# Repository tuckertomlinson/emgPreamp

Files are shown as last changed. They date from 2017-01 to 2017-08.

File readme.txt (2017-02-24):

#Boilerplate:
The files in this repository are my attempt to produce a high-quailty,
buffering amplifier for EMG signals in the laboratory environment. I
am NOT a hardware designer by trade and have not necessarily tested
any of the supplied files for my own purposes, much less yours. I 
make no garauntees that these circuits will be useful or even 
functional.

It is important to also note: I have not designed these
to comply with any FDA standards. Any compliance with said standards
is purely coincidental. These designs are inteded for animal research
and are NOT fit for human recordings in the clinical environment. 

If you choose to use these designs, it is incumbent on you to evaluate
the schematics and test them to ensure they are adequate, in both 
performance and safety, for your task.

I make no promise of support, however, you are welcome to shoot me
an email if you want to use these designs. I might be able to answer
some simple questions.

#The project:
-I need to record 24 differential EMG signals from intramuscular wires
-My signals of interest are in the +/-10mV range
-My ADC system has a +/-5V range, and is remote from the signal source
-I need to buffer and amplify my signals at the source to avoid line
artifacts in my recordings
-The source of the signal is a 50pin samtec 0.05" connector, which I 
	want to convert to something sane like a DB style connector
	so I can use standard cables with my amplified signals

#the solution:
-Signal source connects to a backplane card
-backplane has 6x16pin header sockets 
-each header socket accepts a daughter card that contains 4 differential channels
-Connection to external systems is via DB37 connector
  -24 signal out lines
  -GND and external power in (optional)
  -reference rail out
-daughter cards take:
  - 8 lines of input signal (4 differential signals), 
  - a ground rail, 
  - a power rail
    -the power rail should be in the 5-18V range
  -and a reference rail.
    -the reference rail should be ~ halfway between the ground and power rails
-daughter cards output:
  -4 lines of amplified differential signal centered on the reference rail
-Backplane has a 5pin header socket that is the source of the ground, power and reference rails
  -power connection to external systems will depend on the DAC format you use
  -for a 0V centered ADC (e.g. +/-5V), isolate the ground and power rails from the world, and short the reference to the ADC ground
  -for a positive biased ADC (e.g. 0-10V), connect the ground rail to the DAC ground, and the reference rail to one of the ADC inputs
    -logging the voltage of VRef allows you to subtract in software, recovering the true differential signal
  -The easiest power solution is to simply use 2x 9V batteries in series
    -Power rail is 18V, reference rail is 9V
  -included in the project is a schematic for a power conditioning card
    -card takes in 12-15V power
    -Isolates to internal 12V rail via switchmode isolation supply
    -Uses filters and linear regulators to supply 10V power rail and 5v reference rail to backplane
    -power rail, backplane ground and reference rail are isolated from the supplied power.

The circuit schematics for this project are built in Eagle. 
I have tried to label the lines in each PCB in a sane way, so it should be possible to sort out what's going on. 

In some cases I have needed to create a custom part based on other 
existing libraries in order to get the correct footprint and pinout. 
I have not explicitly included those libraries in this project.

Currently the backplane and daughter cards are tested and functioning as designed. With implanted EMG wires it is common to see single motor unit acticity in the EMG signal. The power-conditioning board is not yet tested

Tucker Tomlinson
tuckertomlinson@gmail.com
Jan 25 2017

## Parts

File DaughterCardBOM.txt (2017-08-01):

item:				supplier:		part number:		notes:
1xPCB				OSH Park		-			OSH accepts eagle files directly, so you can simply upload the brd file to their website
1xsolder mask			OSH stencil		-			you can skip this and apply solder paste by hand, but will have much higher rate of solder-flow errors, particularly under the QVFN-16 amp chips
2x AD8224 instrumentation amp	digikey			AD8224ACPZ-R7CT-ND 	The AD8222 is a pin compatible part with slightly different characteristics (higher gain capability, better CMRR, higher bias current), that may be substituted if desired
1x 2x8pin M 90deg header	digikey			609-3337-ND
8x .01uF 0805 capacitor		digikey			1276-1007-1-ND 		decoupling cap for inputs to amps. no particularly high tolerances needed.
4x 100pF 0805 capacitor		digikey			478-10493-1-ND		RF suppression cap for input lines. Should be significantly lower impedance than caps on input lines.
8x 10k 0.1% 0805 resistor	digikey			P10KDACT-ND		.1% is probably not necessary, but for low volume production, its worth a few extra dollars to match everything
8x 4700pF 1% NP0 0805 capacitor	digikey			490-8288-1-ND		the 1% tolerance isn't necessary, but you need to match capacitor values as well as possible, and the minor increase in cost is offset by the labor savings matching caps
8x 1M 0.1% 0805 resistor	digikey			P1MDACT-ND 		the 0.1% tolerance isn't necessary, but you need to match resistor values as well as possible, and the minor increase in cost is offset by the labor savings matching resistors
4x 499ohm 0805 resistor		digikey			P499CCT-ND 		These set the gain at 100x. Check the AD8224 datasheet to select the correct resistor for alternate gain settings 
4x 49.9ohm 0805 resistor	digikey			P49.9CCT-ND 		inline with output to inhibit ringing

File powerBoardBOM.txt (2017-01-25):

item:				supplier:		part number:		notes:
1xPCB				OSH Park		-			OSH accepts eagle files directly, so you can simply upload the brd file to their website
2x ferrite bead			digikey			732-6713-1-ND 
2x 22uF 16V capacitor		digikey			1276-2909-1-ND 
2x 1uF capacitor		digikey			490-1691-1-ND 
2x 0.33ohm resistor		digikey			RL12S.33FCT-ND
1x 7805 regulator TO252		digikey			MC7805BDTRKGOSCT-ND
1x 7810 regulator TO252		digikey			296-19534-1-ND
1x 12V switchmode isolator	digikey			1470-2537-5-ND		this is a through hole component, but we solder it to the SMT pads, hanging off the board, for packaging
1x 5pin 90deg header		digikey			3M9307-ND

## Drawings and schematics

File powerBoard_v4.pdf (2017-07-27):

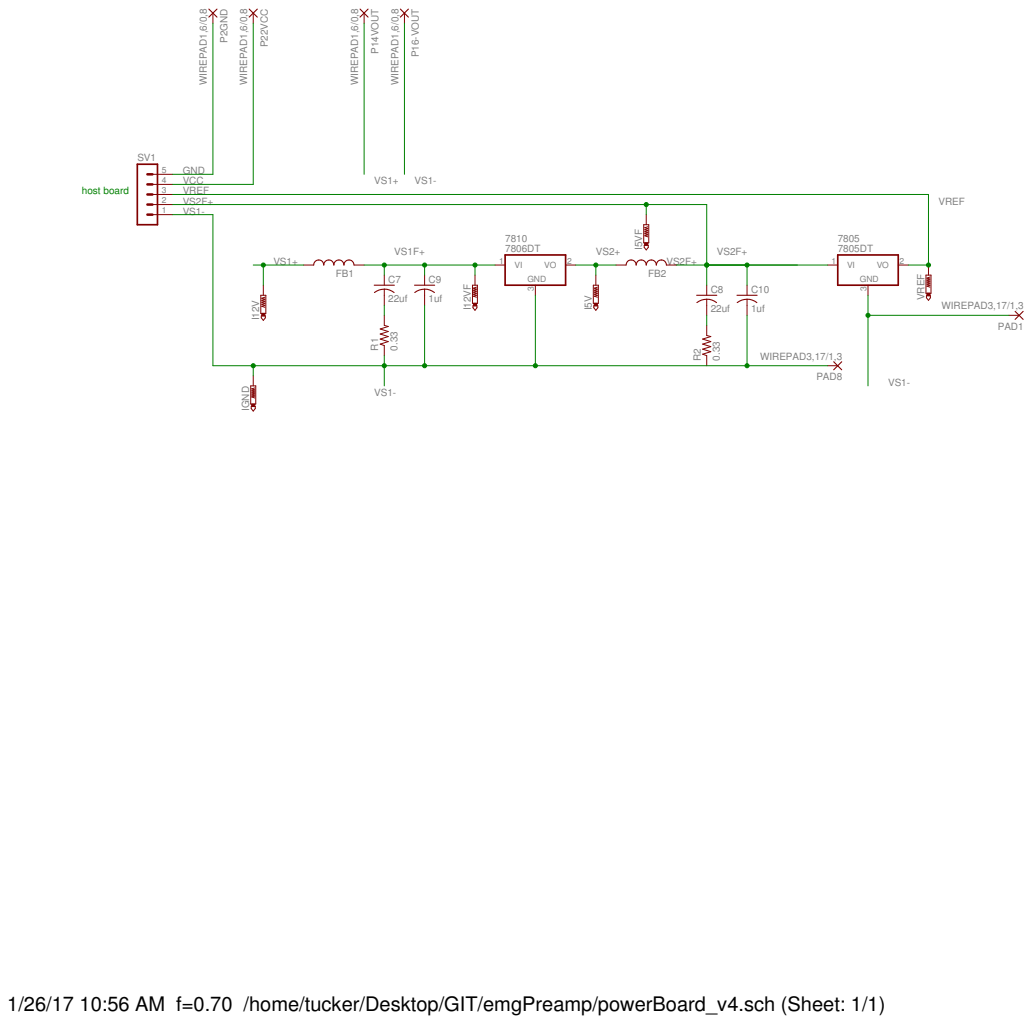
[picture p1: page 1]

1/26/17 10:56 AM f=0.70 /home/tucker/Desktop/GIT/emgPreamp/powerBoard_v4.sch (Sheet: 1/1)

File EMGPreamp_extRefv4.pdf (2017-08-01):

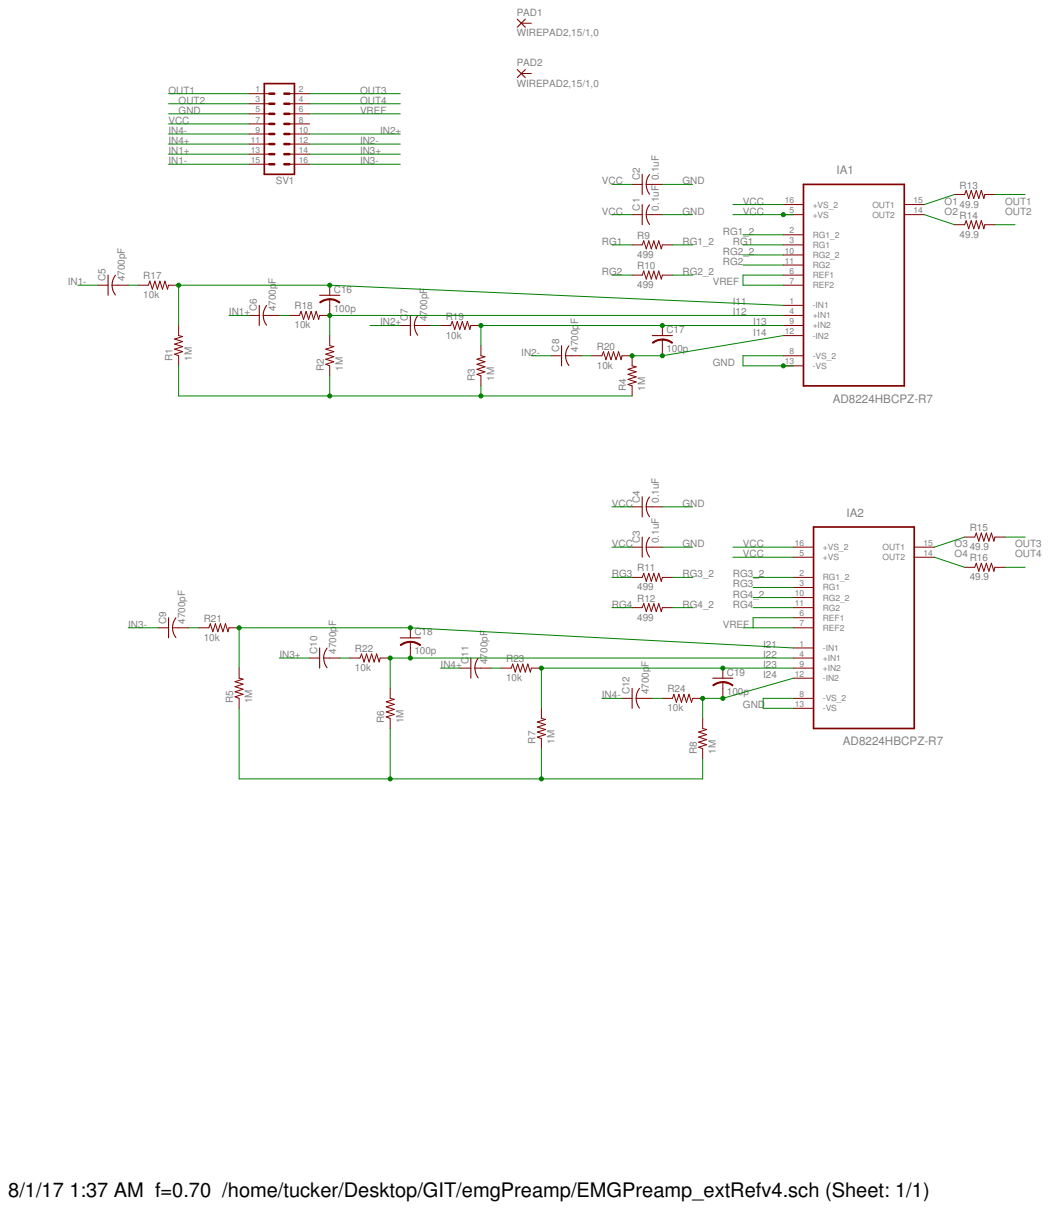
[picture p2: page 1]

8/1/17 1:37 AM f=0.70 /home/tucker/Desktop/GIT/emgPreamp/EMGPreamp_extRefv4.sch (Sheet: 1/1)

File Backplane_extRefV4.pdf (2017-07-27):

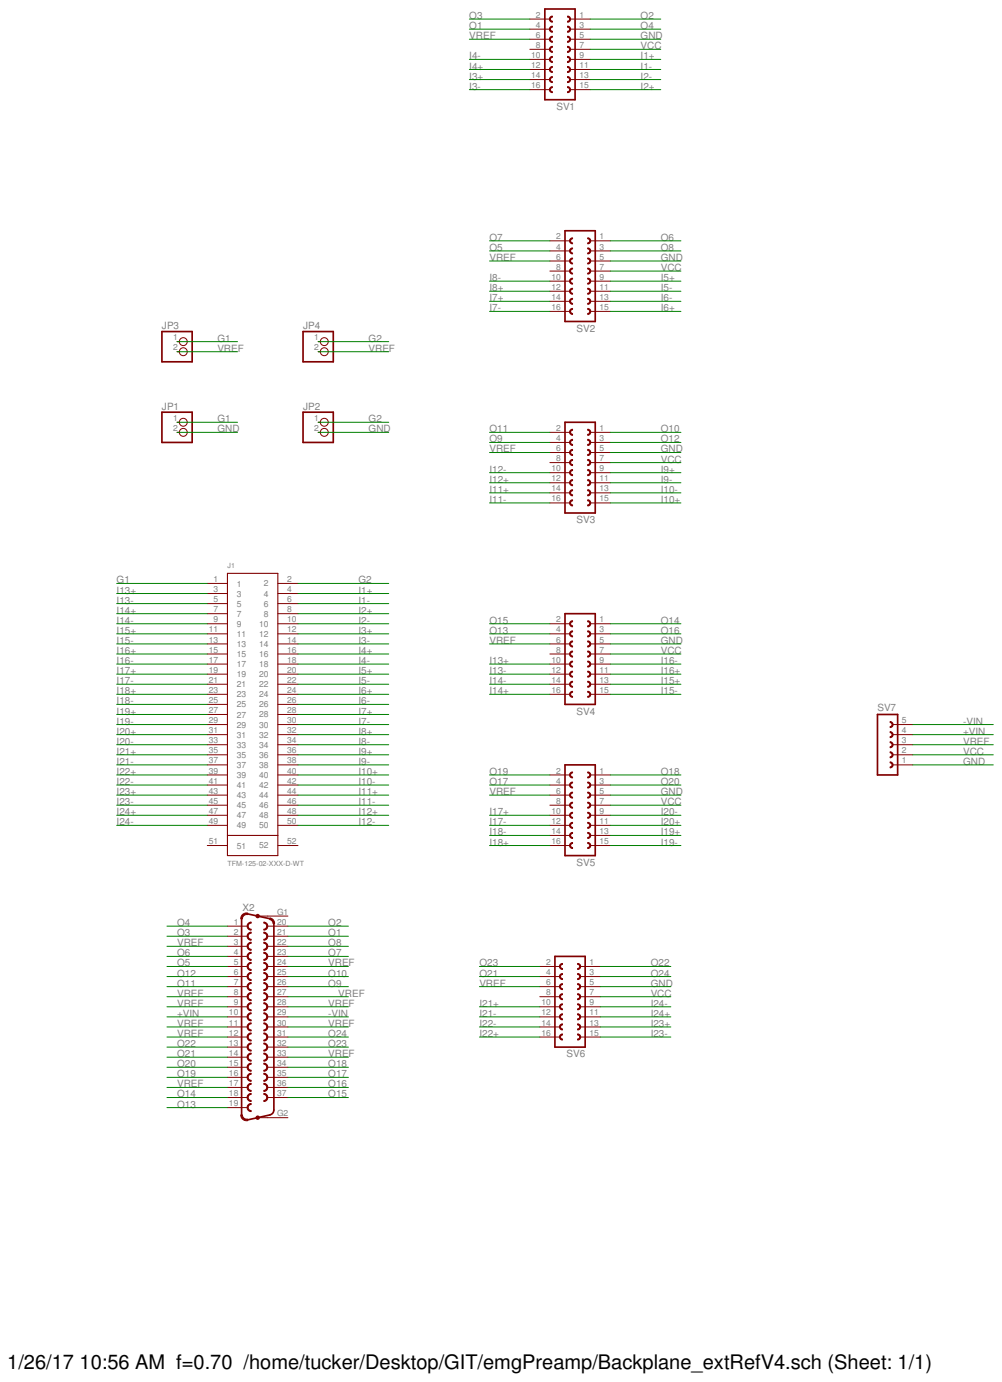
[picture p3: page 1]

1/26/17 10:56 AM f=0.70 /home/tucker/Desktop/GIT/emgPreamp/Backplane_extRefV4.sch (Sheet: 1/1)

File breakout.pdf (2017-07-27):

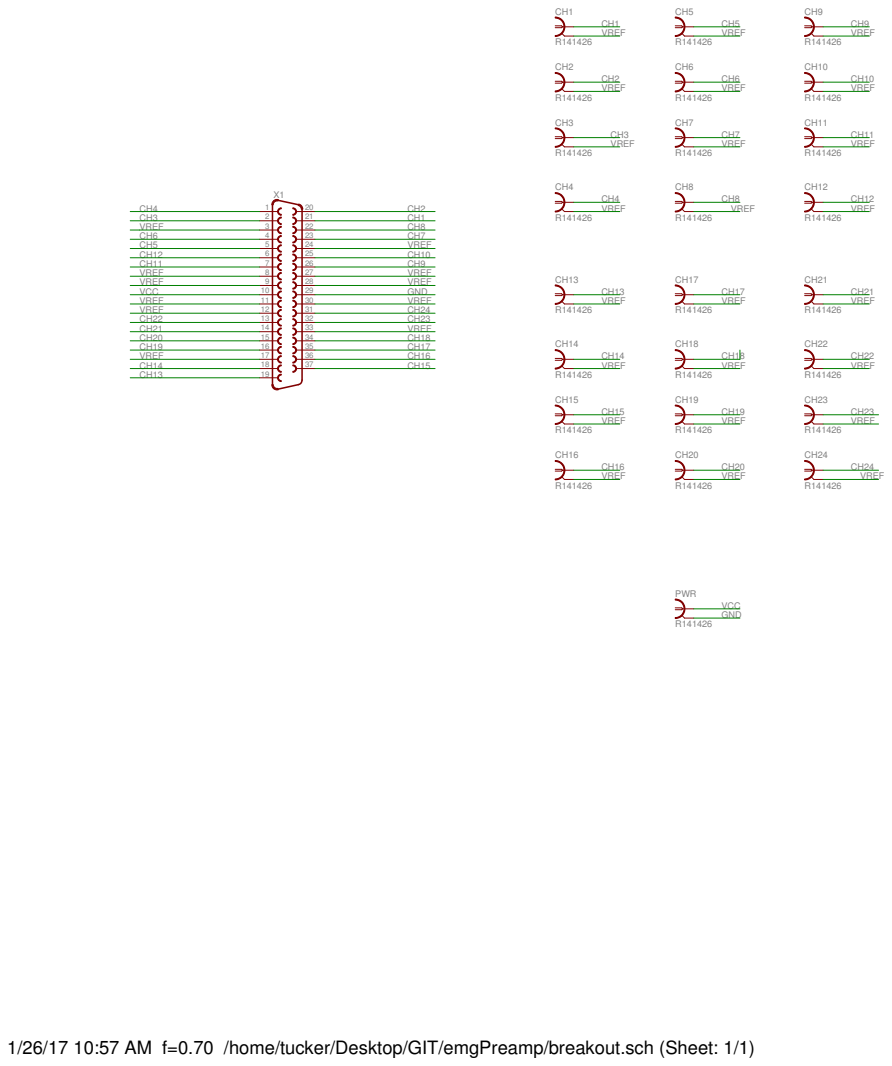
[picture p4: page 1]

1/26/17 10:57 AM f=0.70 /home/tucker/Desktop/GIT/emgPreamp/breakout.sch (Sheet: 1/1)

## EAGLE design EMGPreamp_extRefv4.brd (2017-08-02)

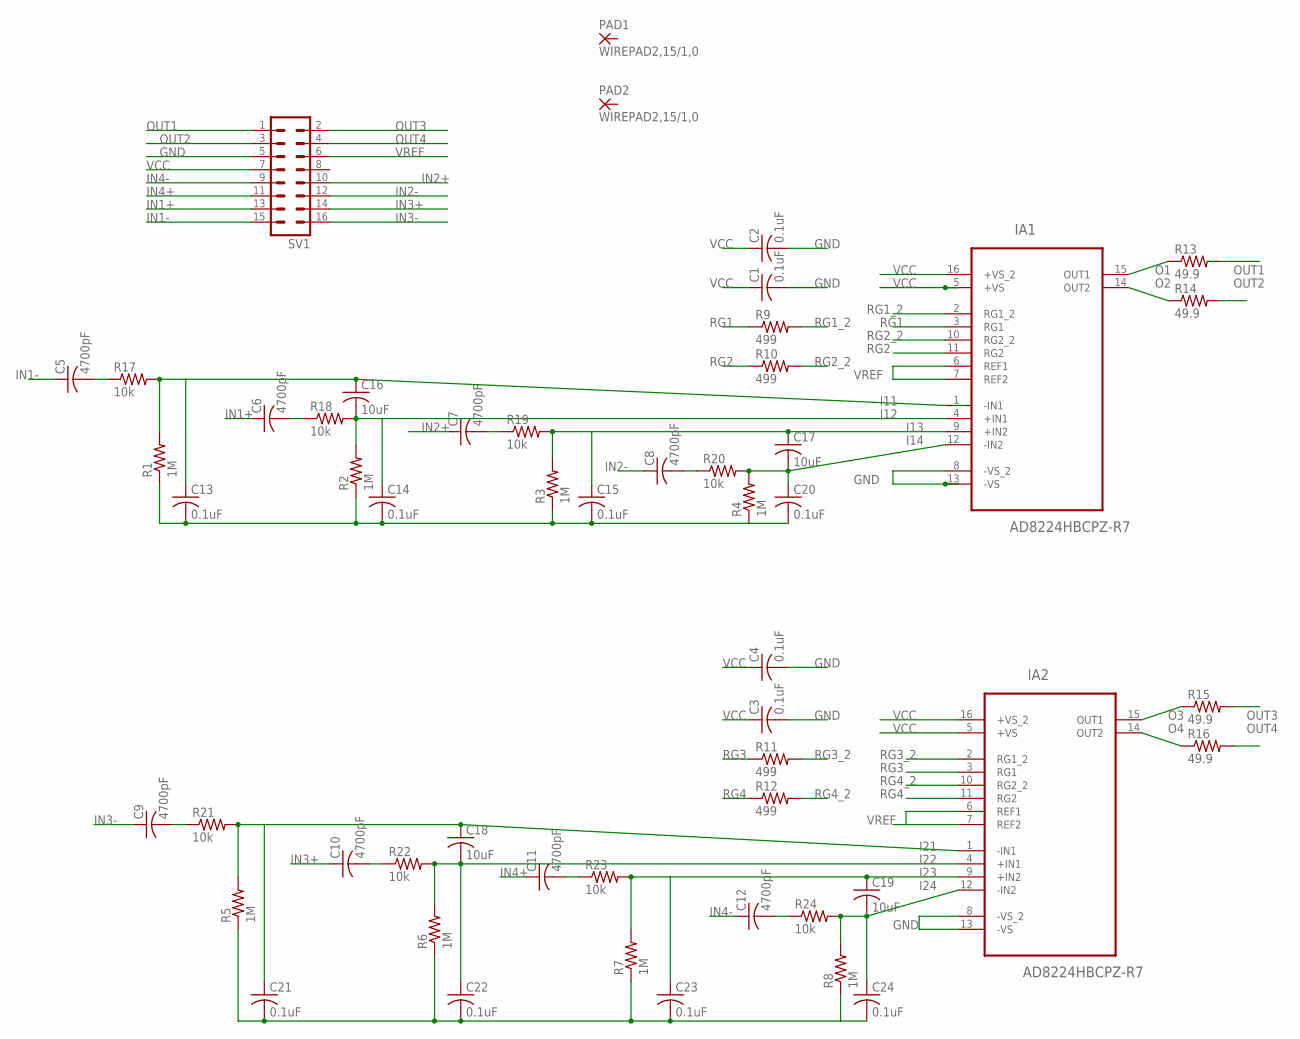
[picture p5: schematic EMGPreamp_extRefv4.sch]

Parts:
C1, C2, C3, C4, C13, C14, C15, C20, C21, C22, C23, C24: 0.1uF; C0805
C5, C6, C7, C8, C9, C10, C11, C12: 4700pF; C0805
C16, C17, C18, C19: 10uF; C0805
IA1, IA2: AD8224HBCPZ-R7; QFN65P400X400X100-16N
PAD1, PAD2: WIREPAD2,15/1,0; 2,15/1,0
R1, R2, R3, R4, R5, R6, R7, R8: 1M; R0805
R9, R10, R11, R12: 499; R0805
R13, R14, R15, R16: 49.9; R0805
R17, R18, R19, R20, R21, R22, R23, R24: 10k; R0805
SV1: MA08-2W

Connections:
GND: C1.2, C2.2, C3.2, C4.2, C13.2, C14.2, C15.2, C20.2, C21.2, C22.2, C23.2, C24.2, IA1.8 (-VS_2), IA1.13 (-VS), IA2.8 (-VS_2), IA2.13 (-VS), R1.1, R2.1, R3.1, R4.1, R5.1, R6.1, R7.1, R8.1, SV1.5
I11: C13.1, C16.1, IA1.1 (-IN1), R1.2, R17.2
I12: C14.1, C16.2, IA1.4 (+IN1), R2.2, R18.2
I13: C15.1, C17.1, IA1.9 (+IN2), R3.2, R19.2
I14: C17.2, C20.1, IA1.12 (-IN2), R4.2, R20.2
I21: C18.1, C21.1, IA2.1 (-IN1), R5.2, R21.2
I22: C18.2, C22.1, IA2.4 (+IN1), R6.2, R22.2
I23: C19.1, C23.1, IA2.9 (+IN2), R7.2, R23.2
I24: C19.2, C24.1, IA2.12 (-IN2), R8.2, R24.2
IN1+: C6.1, SV1.13
IN1-: C5.1, SV1.15
IN2+: C7.1, SV1.10
IN2-: C8.1, SV1.12
IN3+: C10.1, SV1.14
IN3-: C9.1, SV1.16
IN4+: C11.1, SV1.11
IN4-: C12.1, SV1.9
unnamed: C5.2, R17.1
unnamed: C6.2, R18.1
unnamed: C8.2, R20.1
unnamed: C9.2, R21.1
unnamed: C10.2, R22.1
unnamed: C7.2, R19.1
unnamed: C11.2, R23.1
unnamed: C12.2, R24.1
O1: IA1.15 (OUT1), R13.1
O2: IA1.14 (OUT2), R14.1
O3: IA2.15 (OUT1), R15.1
O4: IA2.14 (OUT2), R16.1
OUT1: R13.2, SV1.1
OUT2: R14.2, SV1.3
OUT3: R15.2, SV1.2
OUT4: R16.2, SV1.4
RG1: IA1.3 (RG1), R9.1
RG1_2: IA1.2 (RG1_2), R9.2
RG2: IA1.11 (RG2), R10.1
RG2_2: IA1.10 (RG2_2), R10.2
RG3: IA2.3 (RG1), R11.1
RG3_2: IA2.2 (RG1_2), R11.2
RG4: IA2.11 (RG2), R12.1
RG4_2: IA2.10 (RG2_2), R12.2
VCC: C1.1, C2.1, C3.1, C4.1, IA1.5 (+VS), IA1.16 (+VS_2), IA2.5 (+VS), IA2.16 (+VS_2), SV1.7
VREF: IA1.6 (REF1), IA1.7 (REF2), IA2.6 (REF1), IA2.7 (REF2), SV1.6

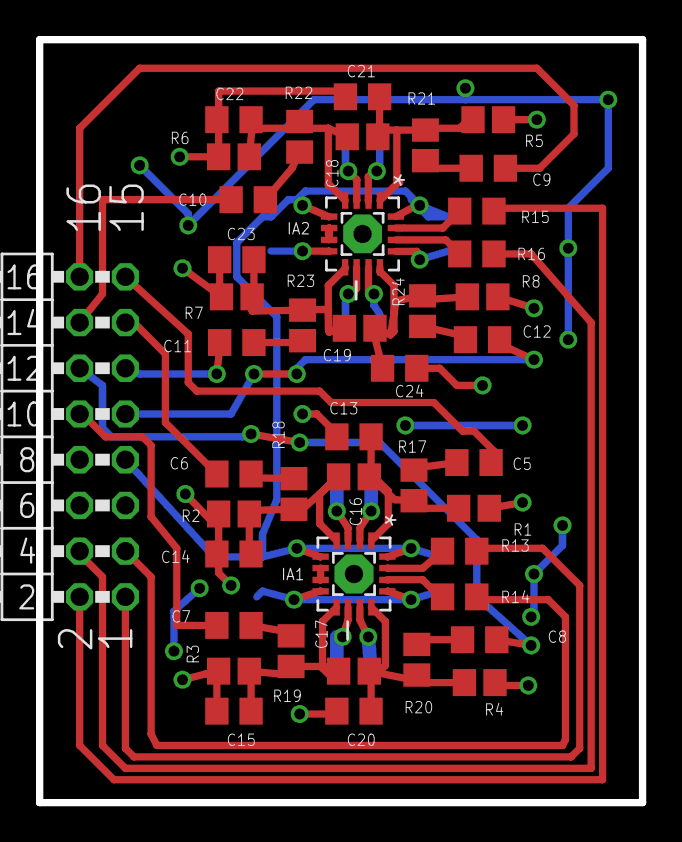
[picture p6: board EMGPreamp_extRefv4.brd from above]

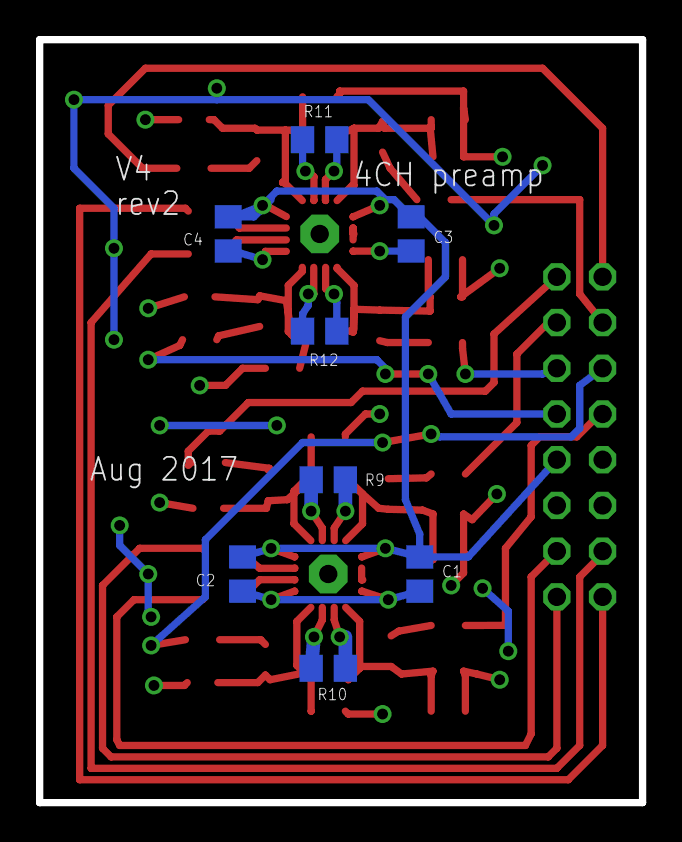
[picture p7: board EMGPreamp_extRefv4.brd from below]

Board: 2 copper layers, 33.5 x 42.4 mm, 53 parts (8 on the bottom side), 43 nets.

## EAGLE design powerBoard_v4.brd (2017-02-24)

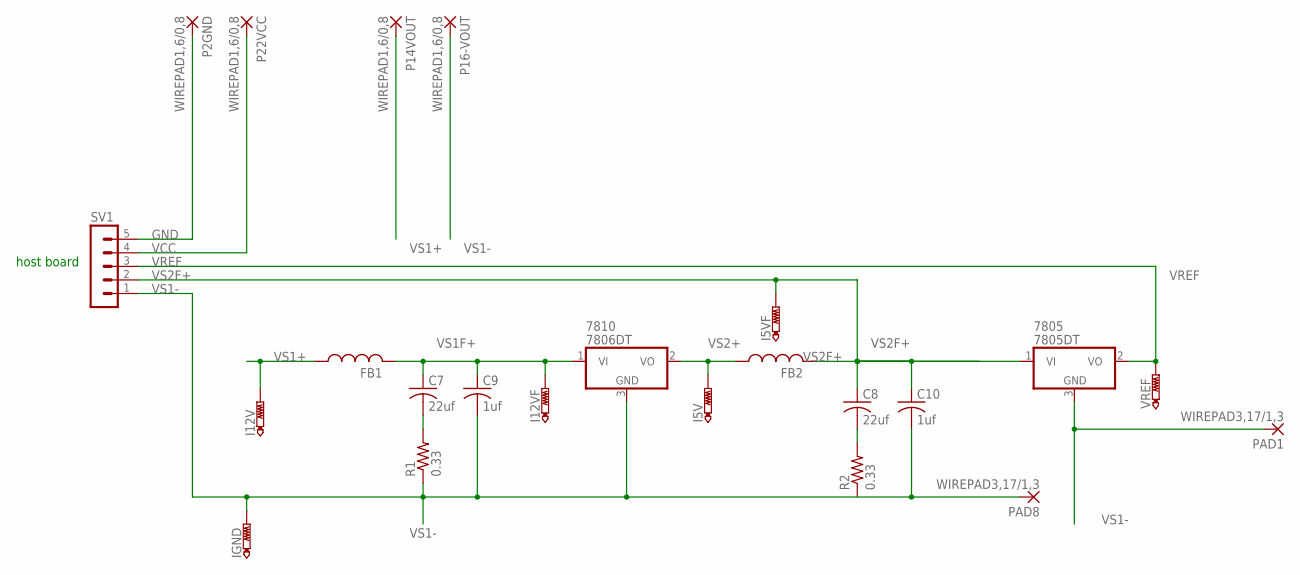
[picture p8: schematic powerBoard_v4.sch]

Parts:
7805: 7805DT; TO252
7810: 7806DT; TO252
C7, C8: 22uf; C0805K
C9, C10: 1uf; C0805K
FB1, FB2: L-USL2012C; L2012C
I5V, I5VF, I12V, I12VF: PTR1PAD1-13; P1-13
IGND: PTR1PAD1-13; P1-13
P2GND, P14VOUT, P16-VOUT, P22VCC: WIREPAD1,6/0,8; 1,6/0,8
PAD1, PAD8: WIREPAD3,17/1,3; 3,17/1,3
R1, R2: 0.33; R2012W
SV1: MA05-1
VREF: PTR1PAD1-13; P1-13

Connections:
GND: P2GND.1, SV1.5
unnamed: C8.2, R2.2
unnamed: C7.2, R1.2
VCC: P22VCC.1, SV1.4
VREF: 7805.2 (VO), SV1.3, VREF.TP
VS1+: FB1.1, I12V.TP, P14VOUT.1
VS1-: 7805.3 (GND), 7810.3 (GND), C9.2, C10.2, IGND.TP, P16-VOUT.1, PAD1.1, PAD8.1, R1.1, SV1.1
VS1F+: 7810.1 (VI), C7.1, C9.1, FB1.2, I12VF.TP
VS2+: 7810.2 (VO), FB2.1, I5V.TP
VS2F+: 7805.1 (VI), C8.1, C10.1, FB2.2, I5VF.TP, SV1.2

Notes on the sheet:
host board

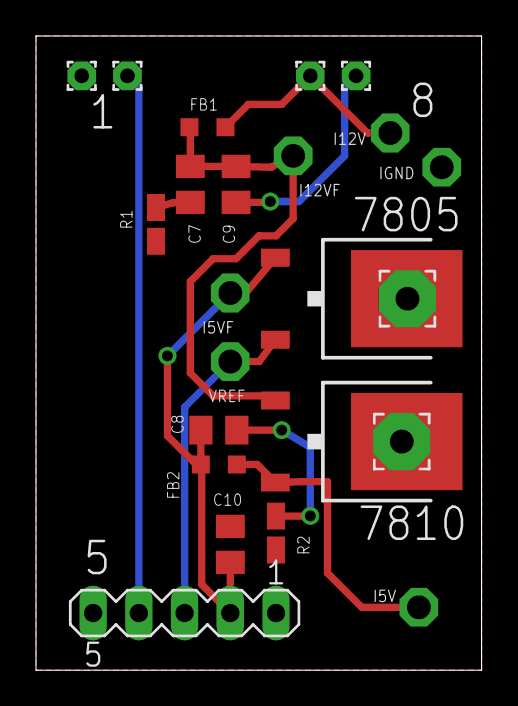
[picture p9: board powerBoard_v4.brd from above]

Board: 2 copper layers, 24.8 x 35.2 mm, 23 parts (0 on the bottom side), 10 nets.

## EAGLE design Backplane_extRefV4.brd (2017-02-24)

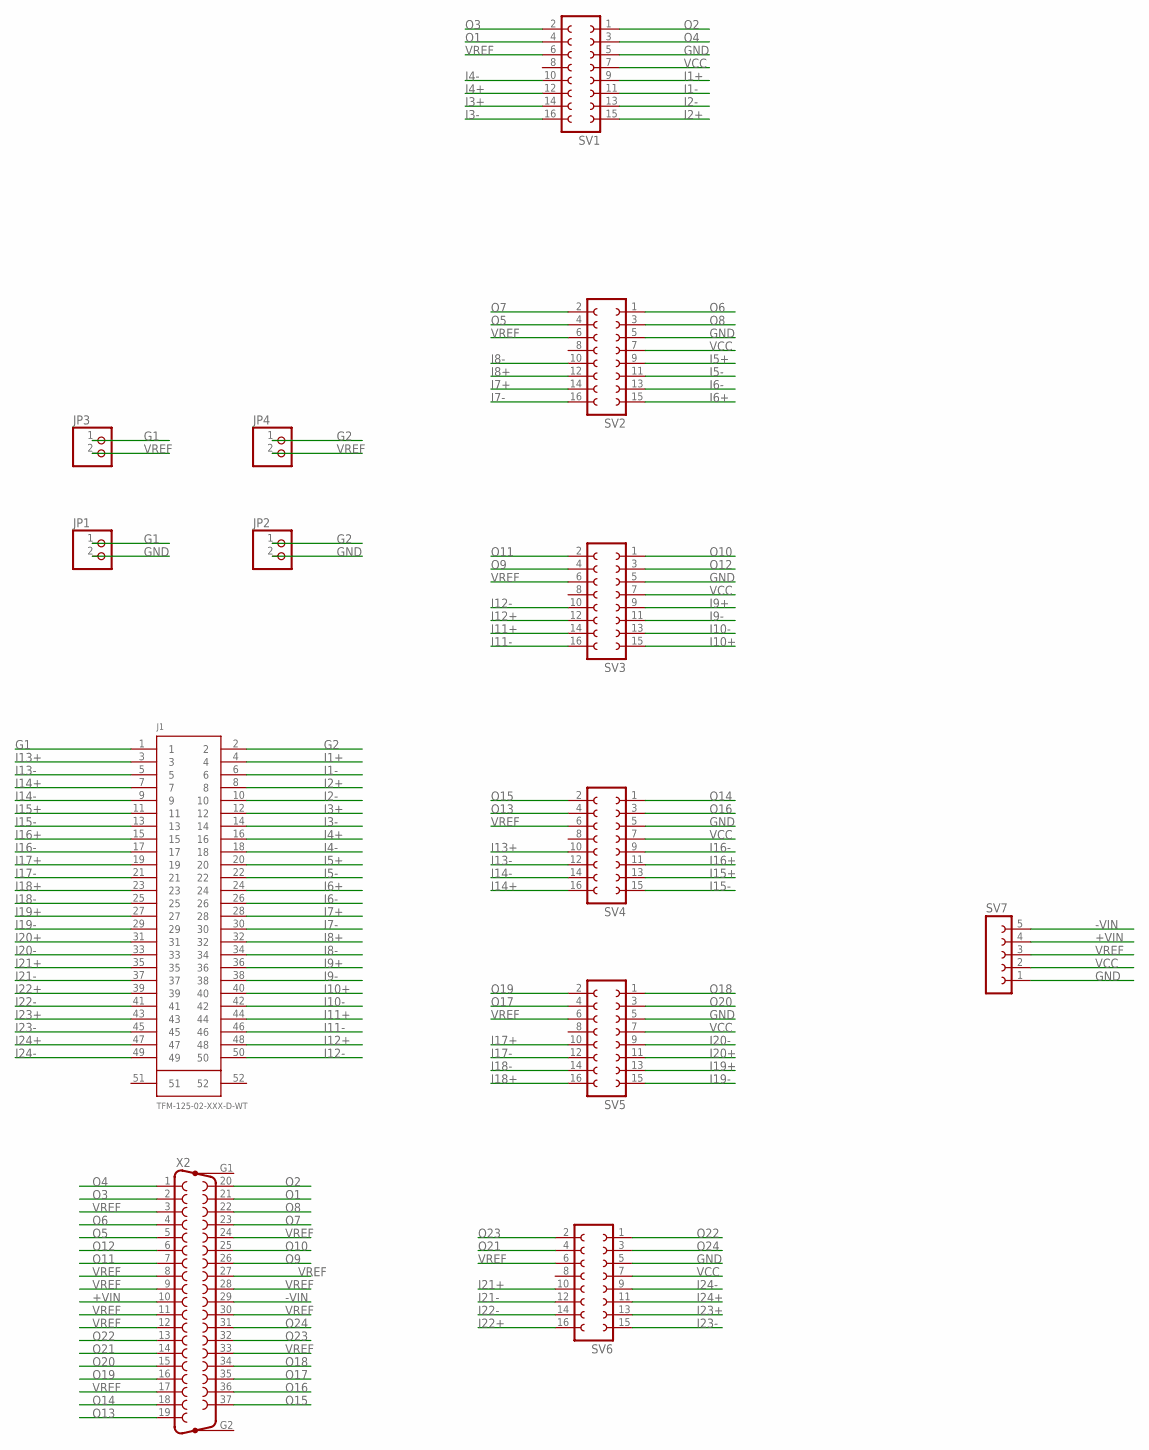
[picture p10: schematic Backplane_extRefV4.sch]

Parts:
J1: TFM-125-02-XXX-D-WT
JP1, JP2, JP3, JP4: PINHD-1X2; 1X02
SV1, SV2, SV3, SV4, SV5, SV6: FE08-2
SV7: FE05-1
X2: F37HP

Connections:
+VIN: SV7.4, X2.10
-VIN: SV7.5, X2.29
G1: J1.1, JP1.1, JP3.1
G2: J1.2, JP2.1, JP4.1
GND: JP1.2, JP2.2, SV1.5, SV2.5, SV3.5, SV4.5, SV5.5, SV6.5, SV7.1
I1+: J1.4, SV1.9
I1-: J1.6, SV1.11
I2+: J1.8, SV1.15
I2-: J1.10, SV1.13
I3+: J1.12, SV1.14
I3-: J1.14, SV1.16
I4+: J1.16, SV1.12
I4-: J1.18, SV1.10
I5+: J1.20, SV2.9
I5-: J1.22, SV2.11
I6+: J1.24, SV2.15
I6-: J1.26, SV2.13
I7+: J1.28, SV2.14
I7-: J1.30, SV2.16
I8+: J1.32, SV2.12
I8-: J1.34, SV2.10
I9+: J1.36, SV3.9
I9-: J1.38, SV3.11
I10+: J1.40, SV3.15
I10-: J1.42, SV3.13
I11+: J1.44, SV3.14
I11-: J1.46, SV3.16
I12+: J1.48, SV3.12
I12-: J1.50, SV3.10
I13+: J1.3, SV4.10
I13-: J1.5, SV4.12
I14+: J1.7, SV4.16
I14-: J1.9, SV4.14
I15+: J1.11, SV4.13
I15-: J1.13, SV4.15
I16+: J1.15, SV4.11
I16-: J1.17, SV4.9
I17+: J1.19, SV5.10
I17-: J1.21, SV5.12
I18+: J1.23, SV5.16
I18-: J1.25, SV5.14
I19+: J1.27, SV5.13
I19-: J1.29, SV5.15
I20+: J1.31, SV5.11
I20-: J1.33, SV5.9
I21+: J1.35, SV6.10
I21-: J1.37, SV6.12
I22+: J1.39, SV6.16
I22-: J1.41, SV6.14
I23+: J1.43, SV6.13
I23-: J1.45, SV6.15
I24+: J1.47, SV6.11
I24-: J1.49, SV6.9
O1: SV1.4, X2.21
O2: SV1.1, X2.20
O3: SV1.2, X2.2
O4: SV1.3, X2.1
O5: SV2.4, X2.5
O6: SV2.1, X2.4
O7: SV2.2, X2.23
O8: SV2.3, X2.22
O9: SV3.4, X2.26
O10: SV3.1, X2.25
O11: SV3.2, X2.7
O12: SV3.3, X2.6
O13: SV4.4, X2.19
O14: SV4.1, X2.18
O15: SV4.2, X2.37
O16: SV4.3, X2.36
O17: SV5.4, X2.35
O18: SV5.1, X2.34
O19: SV5.2, X2.16
O20: SV5.3, X2.15
O21: SV6.4, X2.14
O22: SV6.1, X2.13
O23: SV6.2, X2.32
O24: SV6.3, X2.31
VCC: SV1.7, SV2.7, SV3.7, SV4.7, SV5.7, SV6.7, SV7.2
VREF: JP3.2, JP4.2, SV1.6, SV2.6, SV3.6, SV4.6, SV5.6, SV6.6, SV7.3, X2.3, X2.8, X2.9, X2.11, X2.12, X2.17, X2.24, X2.27, X2.28, X2.30, X2.33

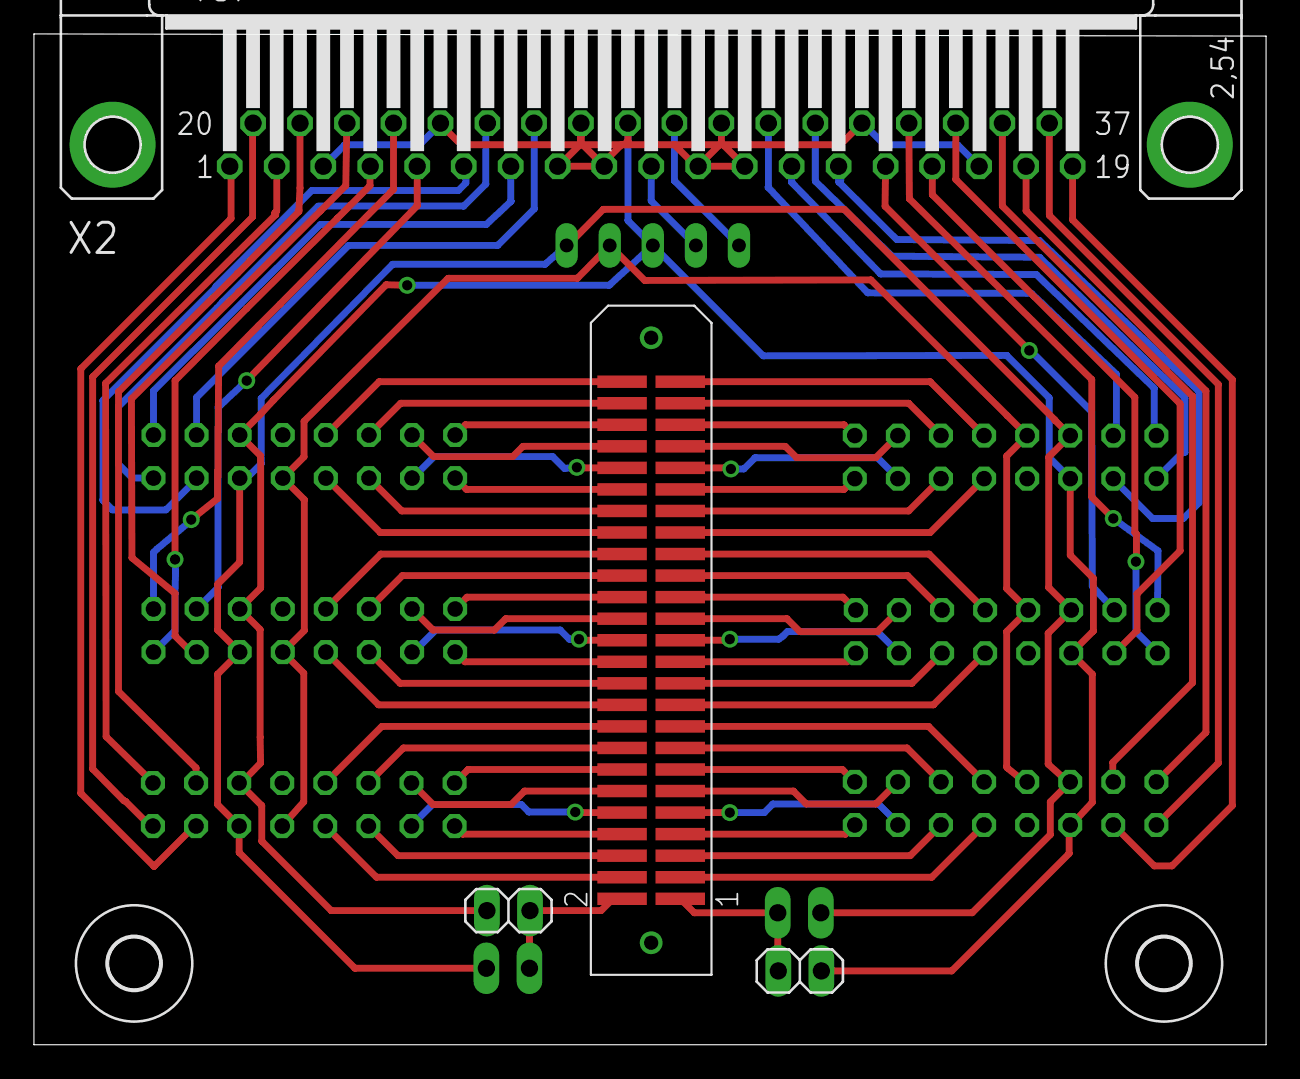
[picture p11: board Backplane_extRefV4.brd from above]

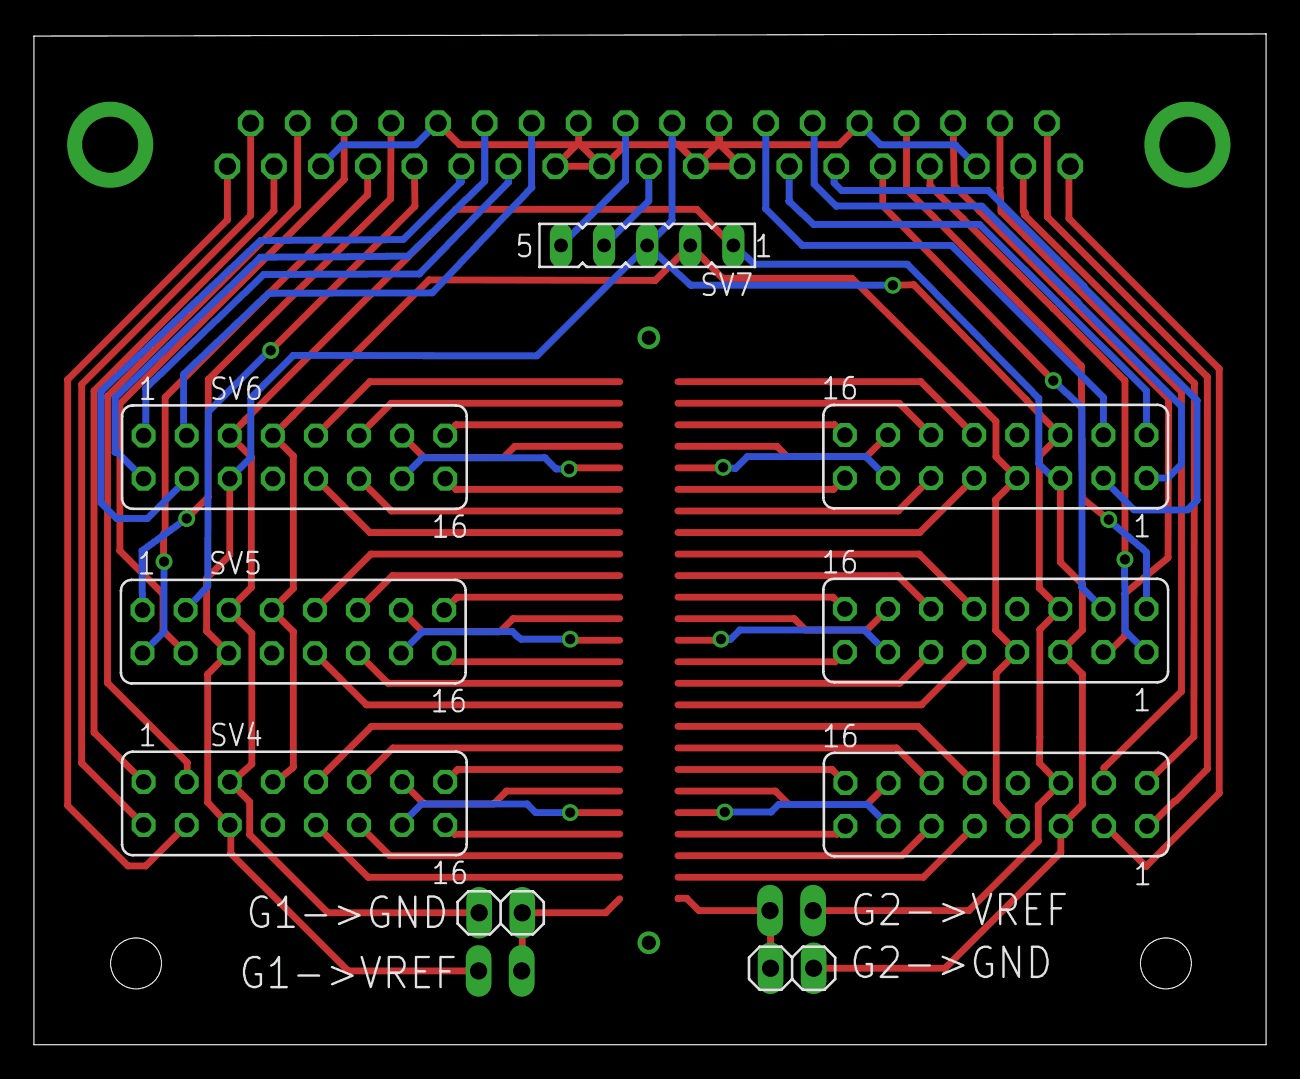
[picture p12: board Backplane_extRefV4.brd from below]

Board: 2 copper layers, 72.6 x 59.6 mm, 15 parts (9 on the bottom side), 79 nets.

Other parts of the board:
U$1, U$2: 3,0

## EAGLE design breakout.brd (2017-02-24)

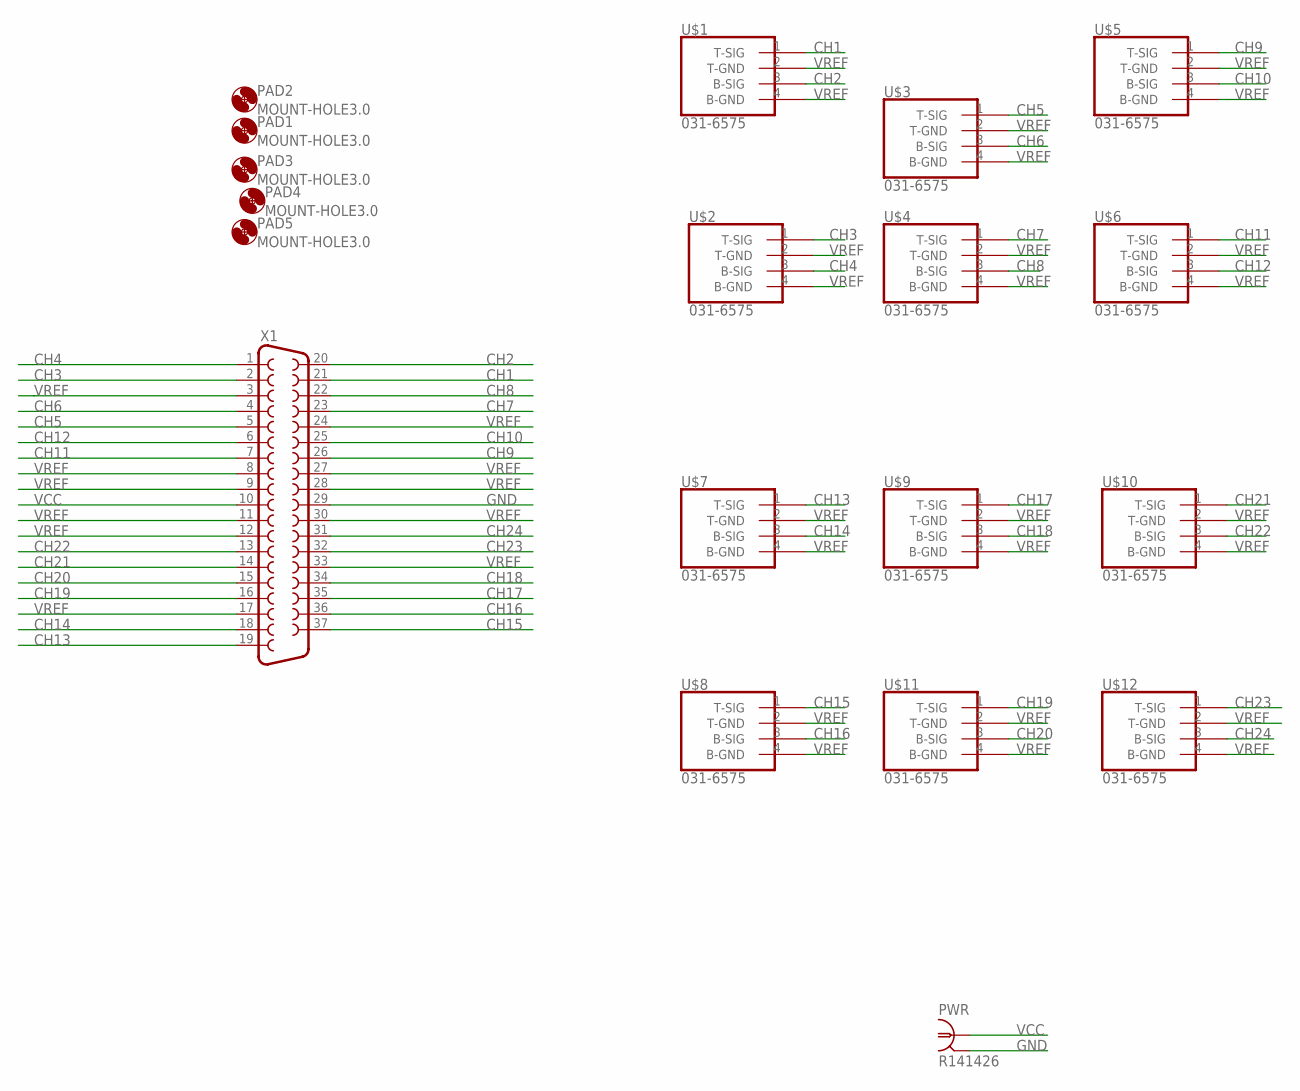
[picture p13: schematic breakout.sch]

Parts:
PAD1, PAD2, PAD3, PAD4, PAD5: MOUNT-HOLE3.0; 3,0
PWR: R141426
U$1, U$2, U$3, U$4, U$5, U$6, U$7, U$8, U$9, U$10, U$11, U$12: 031-6575
X1: F37HP

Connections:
CH1: U$1.1 (T-SIG), X1.21
CH2: U$1.3 (B-SIG), X1.20
CH3: U$2.1 (T-SIG), X1.2
CH4: U$2.3 (B-SIG), X1.1
CH5: U$3.1 (T-SIG), X1.5
CH6: U$3.3 (B-SIG), X1.4
CH7: U$4.1 (T-SIG), X1.23
CH8: U$4.3 (B-SIG), X1.22
CH9: U$5.1 (T-SIG), X1.26
CH10: U$5.3 (B-SIG), X1.25
CH11: U$6.1 (T-SIG), X1.7
CH12: U$6.3 (B-SIG), X1.6
CH13: U$7.1 (T-SIG), X1.19
CH14: U$7.3 (B-SIG), X1.18
CH15: U$8.1 (T-SIG), X1.37
CH16: U$8.3 (B-SIG), X1.36
CH17: U$9.1 (T-SIG), X1.35
CH18: U$9.3 (B-SIG), X1.34
CH19: U$11.1 (T-SIG), X1.16
CH20: U$11.3 (B-SIG), X1.15
CH21: U$10.1 (T-SIG), X1.14
CH22: U$10.3 (B-SIG), X1.13
CH23: U$12.1 (T-SIG), X1.32
CH24: U$12.3 (B-SIG), X1.31
GND: PWR.2, PWR.3 (2), PWR.4 (2), PWR.5 (2), X1.29
VCC: PWR.1, X1.10
VREF: U$1.2 (T-GND), U$1.4 (B-GND), U$2.2 (T-GND), U$2.4 (B-GND), U$3.2 (T-GND), U$3.4 (B-GND), U$4.2 (T-GND), U$4.4 (B-GND), U$5.2 (T-GND), U$5.4 (B-GND), U$6.2 (T-GND), U$6.4 (B-GND), U$7.2 (T-GND), U$7.4 (B-GND), U$8.2 (T-GND), U$8.4 (B-GND), U$9.2 (T-GND), U$9.4 (B-GND), U$10.2 (T-GND), U$10.4 (B-GND), U$11.2 (T-GND), U$11.4 (B-GND), U$12.2 (T-GND), U$12.4 (B-GND), X1.3, X1.8, X1.9, X1.11, X1.12, X1.17, X1.24, X1.27, X1.28, X1.30, X1.33

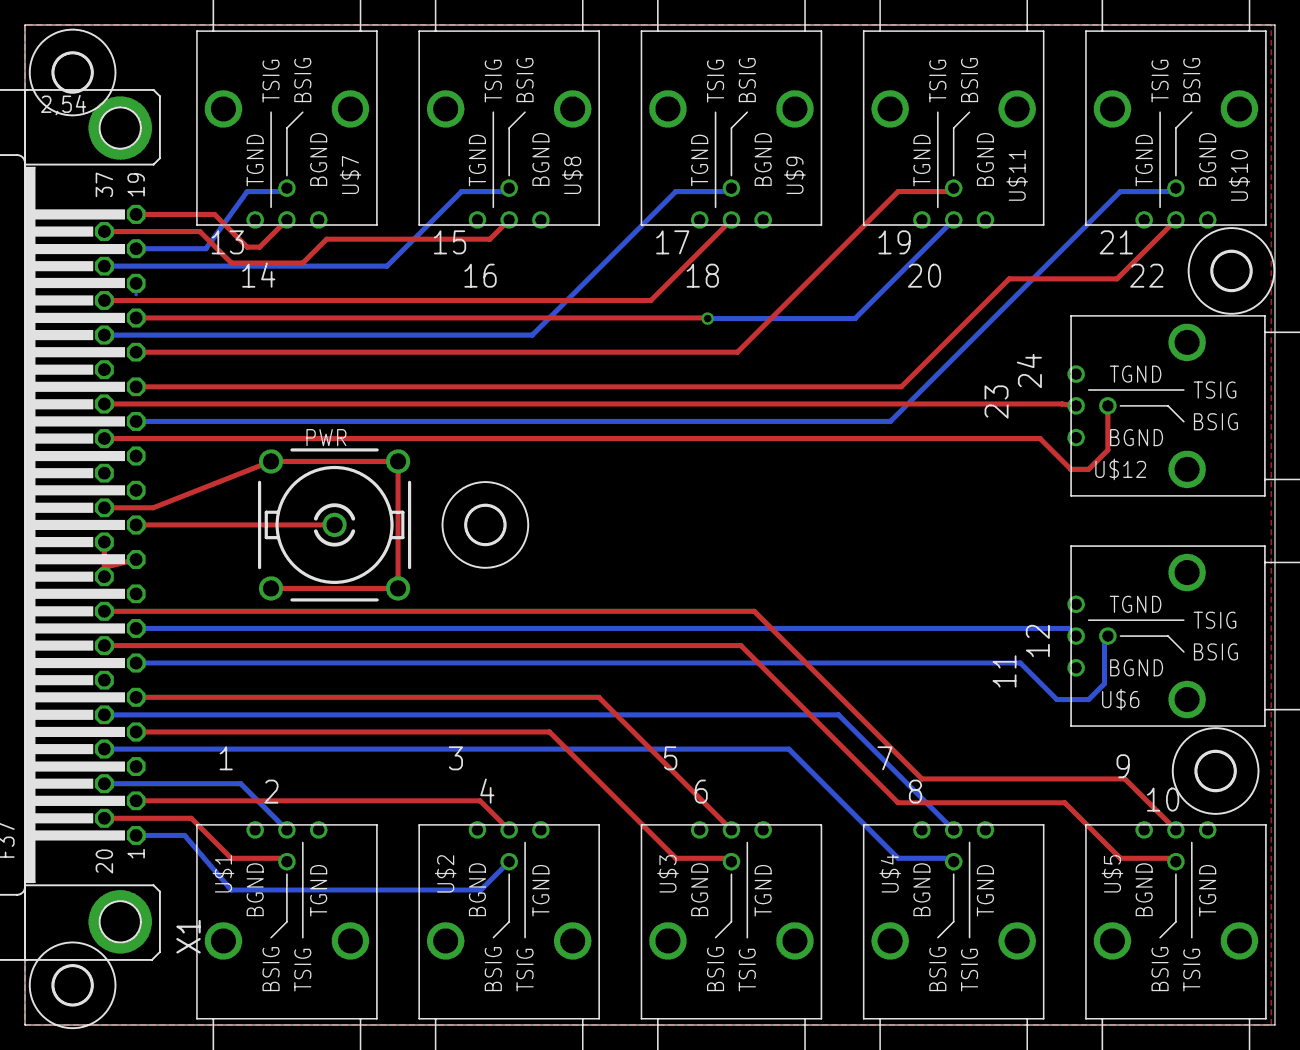
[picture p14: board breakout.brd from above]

Board: 2 copper layers, 100.0 x 80.0 mm, 19 parts (0 on the bottom side), 27 nets.

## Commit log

2016-08-04 added initial boards to repo. Have amp card with/without internal ref line. Have backplanes for with/without internal refs. Have single board solution with all amps on board. None of the current desi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
    [24ch_amp.brd, 24ch_amp.sch, Backplane.brd, Backplane.sch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]
2016-08-04 added a gitignore file to filter irrelevant things like eagle's old save files from the repo
2016-08-16 minor updates to routing. Added DC-DC voltage converter/isolator to backplaneV2 & 24ch brd
    [24ch_amp.brd, 24ch_amp.sch, Backplane_extRefV2.brd, Backplane_extRefV2.sch]
2016-08-18 added new designs that use .1in pitch rather than.05, and added DC-DC isolator for VCC input to backplane
    [24ch_amp.brd, Backplane_extRefV3.brd, Backplane_extRefV3.sch, EMGPreamp_extRefv3.brd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]
2016-08-20 added card to convert 12v DC into isolated 5V & 2.5V DC, including filtering for switching artifacts
    [powerBoard.brd, powerBoard.sch]
2016-08-29 reorganized IO labeling to be consistent on v4 backplane
    [Backplane_extRefV4.brd, Backplane_extRefV4.sch, EMGPreamp_extRefv3.brd]
2016-09-01 new preamp board with capacitive input coupling
    [EMGPreamp_extRefv4.brd, EMGPreamp_extRefv4.sch]
2016-09-01 routing improvements- attempting to isolate inputs from outputs better
    [EMGPreamp_extRefv4.brd]
2016-12-24 updated power board designs: v2 uses low current 2.5v reference, v3 uses 10v rail and 5v ref both with simple linear regulators. Added breakout board to go from DB37 to BNC
    [EMGPreamp_extRefv4.brd, EMGPreamp_extRefv4.sch, breakout.brd, breakout.sch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]
2017-01-25 removed old schematics. Updated readme
    [24ch_amp.brd, 24ch_amp.sch, Backplane.brd, Backplane.sch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]
2017-01-25 updated V4 powerboard to actually include switchmode pads. Added BOM for backplane and daughter card
    [powerBoard_v4.brd, powerBoard_v4.sch]
2017-01-25 added powerboard BOM
2017-02-24 minor labeling and component placement updates. most significant is correcting part position on powerboard so 22uF bypass cap actually connects to ground.
    [Backplane_extRefV4.brd, breakout.brd, breakout.sch, powerBoard_v4.brd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]
2017-08-01 updated design to add RF lowpass and decoupling to input. Also added real ground plane and VREF plane to help isolate inputs from noise
    [EMGPreamp_extRefv4.brd, EMGPreamp_extRefv4.sch]
2017-08-01 updated BOM for daughter cards to include new passives for input filtering
2017-08-02 minor routing changes to increase VREF plane coverage
    [EMGPreamp_extRefv4.brd]
2017-08-02 updated RF input suppression to include decoupling caps to gnd
    [EMGPreamp_extRefv4.brd, EMGPreamp_extRefv4.sch]
